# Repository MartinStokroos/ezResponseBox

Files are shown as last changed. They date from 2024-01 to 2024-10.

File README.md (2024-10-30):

# The ezResponseBox
*An open source Button Response Box for 1-8 buttons based on the Raspberry Pi Pico*

Button response boxes are widely utilized in psychological experiments, typically interfaced as serial devices or as Human Interface Devices (HIDs), such as keyboards or joysticks.

The Raspberry Pi Pico serves as a low-cost microcontroller platform. By incorporating an appropriate number of input buttons (1-8) and a plastic enclosure, a response box can be constructed for under $50, offering specifications comparable to many commercial alternatives. The *ezResponseBox* is compatible with software such as [OpenSesame](https://osdoc.cogsci.nl/), PsychoPy, and E-Prime.

The *ezResponseBox* operates as either a keyboard or joystick-type response box, achieving a typical latency of 1 ms (equivalent to a 1000 Hz update rate). This latency is 10 to 20 times lower than that of standard PC keyboards.

In Keyboard Mode I, the *ezResponseBox* transmits keystrokes corresponding to key numbers 1 to 8 based on the pressed button(s). Simultaneous key presses are communicated within the same USB packet, although this occurrence is rare due to the high input scan rate.

In Keyboard Mode II, the *ezResponseBox* transmits two hexadecimal digits ranging from `00` to `FF`. Applications are responsible for decoding simultaneous key presses.

The advantage of using a joystick HID device lies in its ability to send every state change of the inputs to the host as an eight-bit joystick button state. Decoding of the buttons must be performed within the application program.

The *ezResponseBox* scans eight digital inputs to read the current status of the button knobs. Both Normally Open (NO) and Normally Closed (NC) contacts can be utilized. The type of connected button contacts is determined at power-up. NC contacts facilitate faster detection of response onset. The eight input channels are scanned at a rate of 10 kHz, with readings subjected to debouncing via a FIR digital filter algorithm, incorporating a minimum delay of 200µs which lies within the USB package interval. The debounced information is transmitted in the next available USB packet, with only input state changes sent to the computer.

## Specifications
- USB 2.0 compatible
- works under Windows and Linux
- no drivers needed 
- works as a keyboard or as joystick HID-composite device
- 1ms latency (minimum for HID)
- 10kHz input port scan rate
- integrated switch debouncing filter

GP pin vs. keyboard/joystick button number:

pin: | GP0 | GP1 | GP2 | GP3 | GP4 | GP5 | GP6 | GP7
-------- | --- | --- | --- | --- | --- | --- | --- | ---
keypress | '1' | '2' | '3' | '4' | '5' | '6' | '7' | '8'
hex code | 0x01 | 0x02 | 0x04 | 0x08 | 0x10 | 0x20 | 0x40 | 0x80
joystick button | 0 | 1 | 2 | 3 | 4 | 5 | 6 | 7 

## The Input GPIOs
The input pins are: GP0-GP7. The pull-up function is active on all the inputs to allow direct interfacing to pushbutton switches.

## Using NO/NC Button Contacts
By default, the *ezResponseBox* operates with Normally Open (NO) contacts. If at least one connected switch is of the Normally Closed (NC) type, the *ezResponseBox* will detect this upon startup (immediately after connecting to the USB port), resulting in the inversion of all logic input readings. To maintain simplicity, avoid mixing NO and NC contacts. When using NC-type contacts, ensure that unused input pins are tied to the ground (GND pin).

## The Output GPIOs
The eight debounced inputs are mapped to eight digital outputs, specifically GP8 to GP15. The logic state of these outputs can be inverted (refer to *Configuration Settings* below). The logic level is 3.3V; therefore, level converters and/or line drivers are required to interface with external 5V TTL logic or LED indicators.

## Configuration Settings
Upon connecting the *ezResponseBox* to a computer’s USB port, multiple devices may register with the operating system. The only active device is the one selected via jumper wires or DIP switches. Configuration is established at power-up. Refer to the function table below for detailed configuration settings.

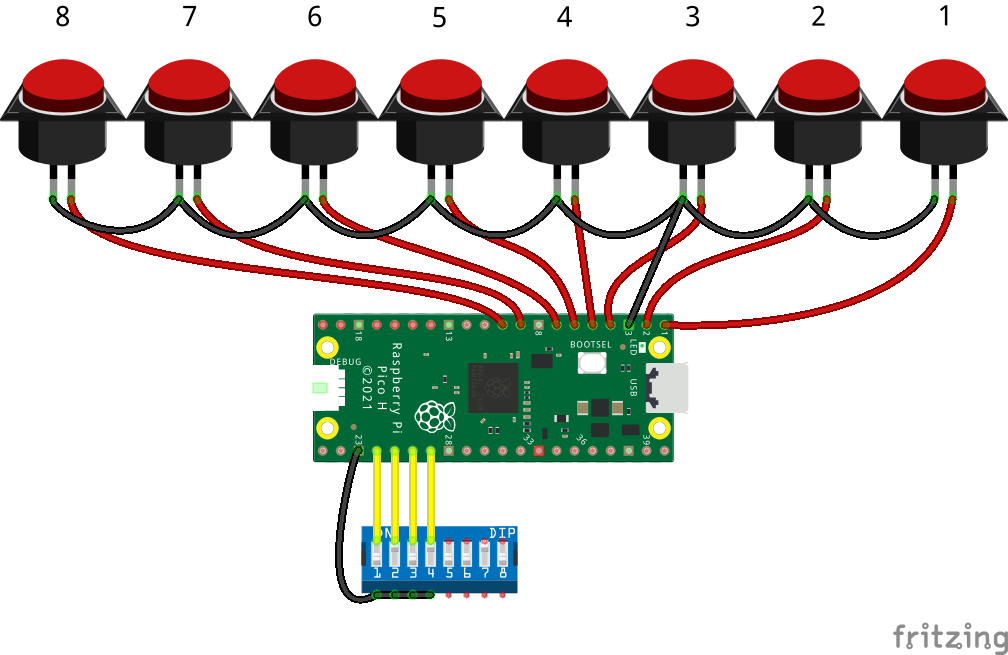
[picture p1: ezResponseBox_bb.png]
wiring diagram


GPIO-pin  | open input | input tied to GND with jumper wire or DIP-switch
--------- | ---------- | ------------------------------------------------
GPIO18 | select keyboard device | select joystick device
GPIO19 | select numerical keys (mode-I) | select hexadecimal digits (mode-II)
GPIO20 | debouncing=ON | debouncing=OFF
GPIO21 | positive logic outputs | negative logic outputs

## Preparing your Raspberry Pico
Hookup one or more buttons to your Pico. Connect the Pico to the PC while pressing and holding the BOOTSEL button. A mass storage device will pop up. Drag the uf2 firmware file into the drive and ready you are! The uf2 firmware file can be found under the release download on this Github page.
This firmware was tested with the Raspberry Pi Pico (without W).

## A 10$ Button Box
A two button response box | bottom side
------------------------- | -----------
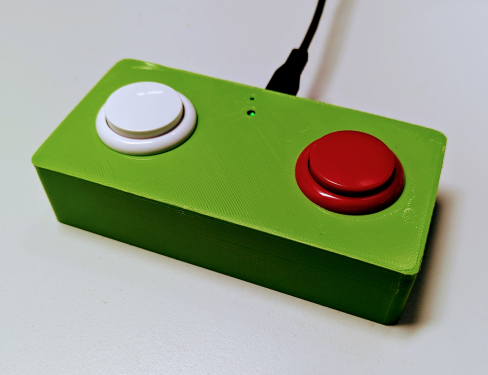
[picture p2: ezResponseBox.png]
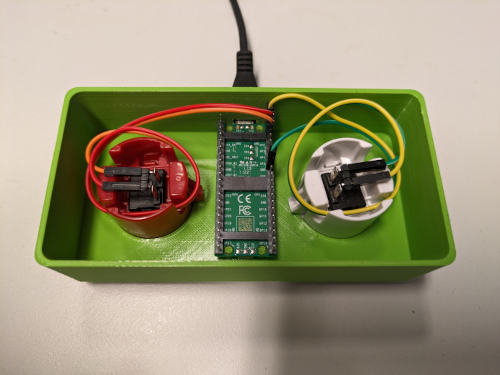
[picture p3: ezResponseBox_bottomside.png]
 | 

## Known bugs
- Displays only one "0"-character in keyboard mode-II for the 0-state code in some text editors or terminal programs. In real, double zeros are sent.
- The color of the prototype:)

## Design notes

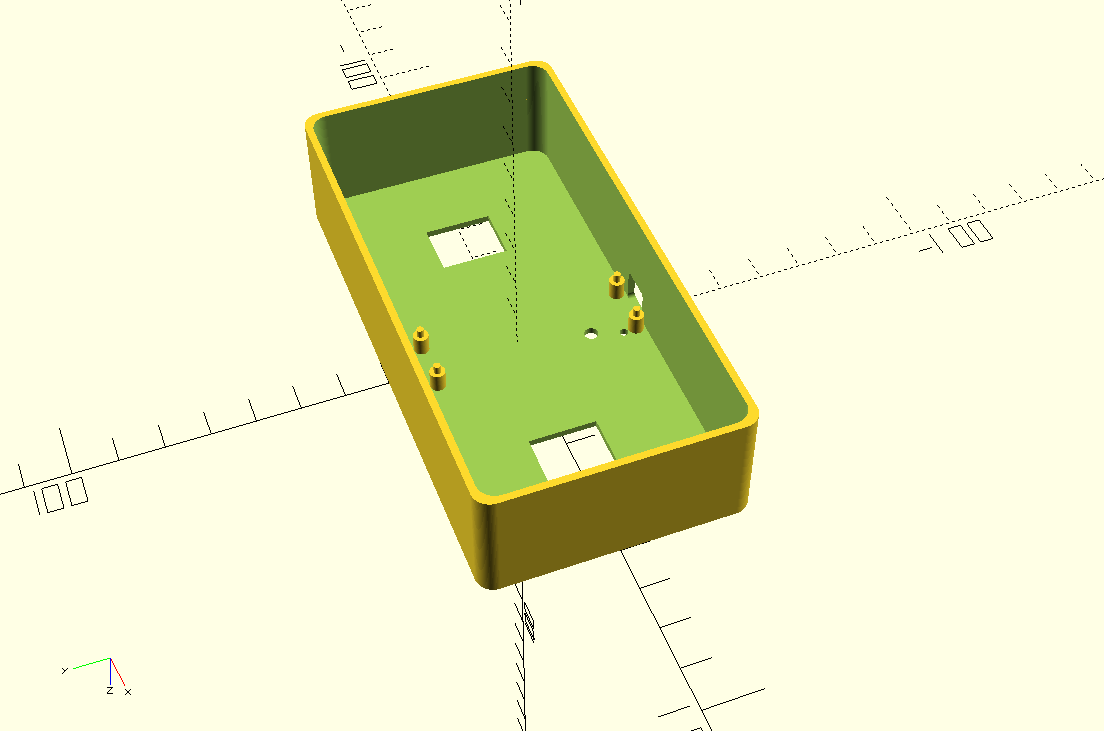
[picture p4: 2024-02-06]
enclosure/ezResponseBox.png

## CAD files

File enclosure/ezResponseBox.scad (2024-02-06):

/*
 * MIT License
 *
 * Copyright (c) 2023 Martin Stokroos
 *
 * Permission is hereby granted, free of charge, to any person obtaining a copy 
 * of this software and associated documentation files (the "Software"), to deal
 * in the Software without restriction, including without limitation the rights 
 * to use, copy, modify, merge, publish, distribute, sublicense, and/or sell 
 * copies of the Software, and to permit persons to whom the Software is 
 * furnished to do so, subject to the following conditions:
 *
 * The above copyright notice and this permission notice shall be included in 
 * all copies or substantial portions of the Software.
 *
 * THE SOFTWARE IS PROVIDED "AS IS", WITHOUT WARRANTY OF ANY KIND, EXPRESS OR 
 * IMPLIED, INCLUDING BUT NOT LIMITED TO THE WARRANTIES OF MERCHANTABILITY, 
 * FITNESS FOR A PARTICULAR PURPOSE AND NONINFRINGEMENT. IN NO EVENT SHALL THE
 * AUTHORS OR COPYRIGHT HOLDERS BE LIABLE FOR ANY CLAIM, DAMAGES OR OTHER
 * LIABILITY, WHETHER IN AN ACTION OF CONTRACT, TORT OR OTHERWISE, ARISING FROM,
 * OUT OF OR IN CONNECTION WITH THE SOFTWARE OR THE USE OR OTHER DEALINGS IN
 * THE SOFTWARE.
 *
 */

// ezResponseBox enclosure for two buttons.
//
// This is a simple OpenSCAD design sketch for a 3D printable response box enclosure.
// This design is screwless. To fixate the pico, melt the (PLA)plastic pins downwards 
// with a (not too) hot iron nail.

length = 120; //dimensions in mm.
width = 60;
height = 28;
wt = 1.6; // wall thickness
poffs = 2.1; // pico spacers, offset from the inner edge (USB-side)
pindia = 1.6; // pico fixation pin diameter
knob_spacing = 34;

difference(){
    union(){
        difference(){
            translate([0,0,-height/2]) roundCornersCube(length, width, height, 4.0); //outline
            translate([0,0,-height/2-wt]) roundCornersCube(length-2*wt, width-2*wt, height, 4.0); //cutout
        }
        // spacers for the PICO
        translate([5.7, -width/2+wt+poffs, -6.0]) cylinder(d=3.5, h=5, center=false, $fn=150); //USB side
        translate([-5.7, -width/2+wt+poffs, -6.0]) cylinder(d=3.5, h=5, center=false, $fn=150); //USB side
        translate([5.7, -width/2+wt+51-poffs, -6.0]) cylinder(d=3.5, h=5, center=false, $fn=150);
        translate([-5.7, -width/2+wt+51-poffs, -6.0]) cylinder(d=3.5, h=5, center=false, $fn=150);
        
        translate([5.7, -width/2+wt+poffs, -8.0]) cylinder(d=pindia, h=6, center=false, $fn=150); //USB side
        translate([-5.7, -width/2+wt+poffs, -8.0]) cylinder(d=pindia, h=6, center=false, $fn=150); //USB side
        translate([5.7, -width/2+wt+51-poffs, -8.0]) cylinder(d=pindia, h=6, center=false, $fn=150);
        translate([-5.7, -width/2+wt+51-poffs, -8.0]) cylinder(d=pindia, h=6, center=false, $fn=150);
    }
      
    // Mark's knob
    //translate([-knob_spacing, 0, 0]) cylinder(d=30.4, h=20, center=true, $fn=150);
    //translate([knob_spacing, 0, 0]) cylinder(d=30.4, h=20, center=true, $fn=150);
    
    // Standard knobs, use your own knob cut out pattern.
    translate([34, 0, 0])cube([12.5, 15.5, 10], center=true);
    translate([-34, 0, 0])cube([12.5, 15.5, 10], center=true);
    
    // Opening for the USB connector.
    translate([0, -width/2+0.2, -8.0/2-wt]) rotate([90,0,0]) roundCornersCube(8.0, 8, 3.0, 1);
    // Hole for pico bootsel button.
    translate([3.7, -width/2+wt+poffs+10, -3]) cylinder(d=3.2, h=6, center=false, $fn=150);
    // Hole for pico LED.
    translate([6, -width/2+wt+poffs+3, -3]) cylinder(d=2, h=6, center=false, $fn=150);
}



/*
roundCornersCube is licensed under the GNU license.

Copyright (C) 2011 Sergio Vilches

This program is free software: you can redistribute it and/or modify it under the terms of the GNU General Public License as published by the Free Software Foundation, either version 3 of the License, or (at your option) any later version.
This program is distributed in the hope that it will be useful, but WITHOUT ANY WARRANTY; without even the implied warranty of MERCHANTABILITY or FITNESS FOR A PARTICULAR PURPOSE. See the GNU General Public License for more details. You should have received a copy of the GNU General Public License along with this program. If not, see <http://www.gnu.org/licenses/>.
Contact: s.vilches.e@gmail.com


    ----------------------------------------------------------- 
                 Round Corners Cube (Extruded)            
      roundCornersCube(x,y,z,r) Where:                        
         - x = Xdir width                                     
         - y = Ydir width                                     
         - z = Height of the cube                             
         - r = Rounding radious                               
                                                              
      Example: roundCornerCube(10,10,2,1);                    
     *Some times it's needed to use F6 to see good results!   
 	 ---------------------------------------------------------- 
*/

module createMeniscus(h,radius) // This module creates the shape that needs to be substracted from a cube to make its corners rounded.
difference(){        //This shape is basicly the difference between a quarter of cylinder and a cube
   translate([radius/2+0.1,radius/2+0.1,0]){
      cube([radius+0.2,radius+0.1,h+0.2],center=true);         // All that 0.x numbers are to avoid "ghost boundaries" when substracting
   }

   cylinder(h=h+0.2,r=radius,$fn = 100,center=true);
}


module roundCornersCube(x,y,z,r)  // Now we just substract the shape we have created in the four corners
difference(){
   cube([x,y,z], center=true);

translate([x/2-r,y/2-r]){  // We move to the first corner (x,y)
      rotate(0){  
         createMeniscus(z,r); // And substract the meniscus
      }
   }
   translate([-x/2+r,y/2-r]){ // To the second corner (-x,y)
      rotate(90){
         createMeniscus(z,r); // But this time we have to rotate the meniscus 90 deg
      }
   }
      translate([-x/2+r,-y/2+r]){ // ... 
      rotate(180){
         createMeniscus(z,r);
      }
   }
      translate([x/2-r,-y/2+r]){
      rotate(270){
         createMeniscus(z,r);
      }
   }
}

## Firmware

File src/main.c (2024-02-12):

/* 
 * The MIT License (MIT)
 *
 * Copyright (c) 2019 Ha Thach (tinyusb.org)
 *
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
 */
 
/*
 * MIT License
 *
 * Copyright (c) 2023 Martin Stokroos (ezResponseBox)
 *
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
 */

#include <stdlib.h>
#include <stdio.h>
#include <string.h>
#include "hardware/gpio.h"
#include "pico/util/queue.h"

#include "bsp/board.h"
#include "tusb.h"
#include "usb_descriptors.h"

#define HZ 100  //digital input sampling delay in us.
#define NCHAN 8 //max number of input/output channels = 8
#define FIRST_GPIO_IN 0
#define FIRST_GPIO_OUT (FIRST_GPIO_IN + 8)
#define RANGE_GPIO 0xFFFF
#define KEY_JOY_SEL_PIN 18
#define KEY_MODE_SEL_PIN 19
#define DEBOUNCE_SEL_PIN 20
#define INVERT_OUTPUTS_SEL_PIN 21

//--------------------------------------------------------------------+
// MACRO CONSTANT TYPEDEF PROTYPES
//--------------------------------------------------------------------+

/* Blink pattern
 * - 250 ms  : device not mounted
 * - 1000 ms : device mounted
 * - 2500 ms : device is suspended
 */
enum {
  BLINK_NOT_MOUNTED = 250,
  BLINK_MOUNTED = 1000,
  BLINK_SUSPENDED = 2500,
};

// prototypes
void led_blinking_task(void);
void hid_task(void);
static void send_hid_report(uint8_t report_id);
bool timer_callback(repeating_timer_t *rt);
void to_hex(uint8_t* in, uint8_t* out);
void to_keycode(uint8_t* in, size_t insz, uint8_t* out);

// globals
static uint32_t blink_interval_ms = BLINK_NOT_MOUNTED;
static uint32_t portsAll;
static uint8_t newEvent, lastEvent, xMask;
static bool eventUpdate;
typedef struct {
  bool ncContacts;
  bool deviceMode;
  bool keyMode;
  bool debounceOn;
  bool invertOp;
} ezConfig;
ezConfig config;

static uint8_t window[8] = {0, 0, 0, 0, 0, 0, 0, 0}; // store 8-ch parallel window data
static const uint8_t filtered[32] =
{
  0,  //00000
  0,  //00001
  0,  //00010
  1,  //00011
  0,  //00100
  1,  //00101
  1,  //00110
  1,  //00111
  0,  //01000
  1,  //01001
  1,  //01010
  1,  //01011
  1,  //01100
  1,  //01101
  1,  //01110
  1,  //01111
  0,  //10000
  0,  //10001
  0,  //10010
  1,  //10011
  0,  //10100
  1,  //10101
  1,  //10110
  1,  //10111
  0,  //11000
  1,  //11001
  1,  //11010
  1,  //11011
  1,  //11100
  1,  //11101
  1,  //11110
  1   //11111
};


/*------------- MAIN -------------*/
int main(void)
{
  gpio_init(KEY_JOY_SEL_PIN);
  gpio_init(KEY_MODE_SEL_PIN);
  gpio_init(DEBOUNCE_SEL_PIN);
  gpio_init(INVERT_OUTPUTS_SEL_PIN);
  gpio_set_dir(KEY_JOY_SEL_PIN, GPIO_IN);
  gpio_set_dir(KEY_MODE_SEL_PIN, GPIO_IN);
  gpio_set_dir(DEBOUNCE_SEL_PIN, GPIO_IN);
  gpio_set_dir(INVERT_OUTPUTS_SEL_PIN, GPIO_IN);
  gpio_pull_up(KEY_JOY_SEL_PIN);
  gpio_pull_up(KEY_MODE_SEL_PIN);
  gpio_pull_up(DEBOUNCE_SEL_PIN);
  gpio_pull_up(INVERT_OUTPUTS_SEL_PIN);

  // Read the hardware configuration status
  config.deviceMode = gpio_get(KEY_JOY_SEL_PIN);
  config.keyMode = gpio_get(KEY_MODE_SEL_PIN);
  config.debounceOn = gpio_get(DEBOUNCE_SEL_PIN);
  config.invertOp = gpio_get(INVERT_OUTPUTS_SEL_PIN);

  for (int gpio = FIRST_GPIO_IN; gpio < FIRST_GPIO_IN + NCHAN; gpio++)
  {
    gpio_init(gpio);
    gpio_set_dir(gpio, GPIO_IN);
    gpio_pull_up(gpio);
  }

  for (int gpio = FIRST_GPIO_OUT; gpio < FIRST_GPIO_OUT + NCHAN; gpio++)
  {
    gpio_init(gpio);
    gpio_set_dir(gpio, GPIO_OUT);
    if(!config.invertOp) {
      gpio_set_outover(gpio, GPIO_OVERRIDE_INVERT); //invert output channels
    }
  }  

  // Detect if one or more switches are NC and pulling down the input.
  portsAll = ~gpio_get_all(); // Read all gpio's (29-0) at once and bitwise invert.
  portsAll = portsAll >> FIRST_GPIO_IN;
  if ((portsAll & 0xFF) > 0) // Use bitmask for 8 bits. (Size of NCHAN could be different!)
  {
    config.ncContacts = true;
  }

  board_init();
  tusb_init();

  repeating_timer_t timer;
  // negative timeout means exact delay in us (rather than delay between callbacks)
  if (!add_repeating_timer_us(-HZ, timer_callback, NULL, &timer)) {
    //printf("Failed to add timer\n");
    return 1;
  }

  while (1)
  {
    tud_task(); // tinyusb device task
    led_blinking_task();

    hid_task();
    //cancel_repeating_timer(&timer);
  }
}



//--------------------------------------------------------------------+
// Device callbacks
//--------------------------------------------------------------------+

// Invoked when device is mounted
void tud_mount_cb(void)
{
  blink_interval_ms = BLINK_MOUNTED;
}

// Invoked when device is unmounted
void tud_umount_cb(void)
{
  blink_interval_ms = BLINK_NOT_MOUNTED;
}

// Invoked when usb bus is suspended
// remote_wakeup_en : if host allow us  to perform remote wakeup
// Within 7ms, device must draw an average of current less than 2.5 mA from bus
void tud_suspend_cb(bool remote_wakeup_en)
{
  (void) remote_wakeup_en;
  blink_interval_ms = BLINK_SUSPENDED;
}

// Invoked when usb bus is resumed
void tud_resume_cb(void)
{
  blink_interval_ms = BLINK_MOUNTED;
}


//--------------------------------------------------------------------+
// USB HID
//--------------------------------------------------------------------+

// Invoked when sent REPORT successfully to host
// Application can use this to send the next report
// Note: For composite reports, report[0] is report ID
void tud_hid_report_complete_cb(uint8_t instance, uint8_t const* report, uint16_t len)
{
  (void) instance;
  (void) len;
}


// Invoked when received GET_REPORT control request
// Application must fill buffer report's content and return its length.
// Return zero will cause the stack to STALL request
uint16_t tud_hid_get_report_cb(uint8_t instance, uint8_t report_id, hid_report_type_t report_type, uint8_t* buffer, uint16_t reqlen)
{
  // TODO not Implemented
  (void) instance;
  (void) report_id;
  (void) report_type;
  (void) buffer;
  (void) reqlen;

  return 0;
}


// Invoked when received SET_REPORT control request or
// received data on OUT endpoint ( Report ID = 0, Type = 0 )
void tud_hid_set_report_cb(uint8_t instance, uint8_t report_id, hid_report_type_t report_type, uint8_t const* buffer, uint16_t bufsize)
{
  (void) instance;

  if (report_type == HID_REPORT_TYPE_OUTPUT)
  {
    // Set keyboard LED e.g Capslock, Numlock etc...
    if (report_id == REPORT_ID_KEYBOARD)
    {
      // bufsize should be (at least) 1
      if ( bufsize < 1 ) return;

      uint8_t const kbd_leds = buffer[0];

      if (kbd_leds & KEYBOARD_LED_CAPSLOCK)
      {
        // Capslock On: disable blink, turn led on
        blink_interval_ms = 0;
        board_led_write(true);
      } else
      {
        // Caplocks Off: back to normal blink
        board_led_write(false);
        blink_interval_ms = BLINK_MOUNTED;
      }
    }
  }
}



//--------------------------------------------------------------------+
// BLINKING TASK
//--------------------------------------------------------------------+
void led_blinking_task(void)
{
  static uint32_t start_ms = 0;
  static bool led_state = false;

  // blink is disabled
  if (!blink_interval_ms) return;

  // Blink every interval ms
  if ( board_millis() - start_ms < blink_interval_ms) return; // not enough time
  start_ms += blink_interval_ms;

  board_led_write(led_state);
  led_state = 1 - led_state; // toggle
}



//--------------------------------------------------------------------+
// HID TASK
//--------------------------------------------------------------------+
void hid_task(void)
{
  // Remote wakeup
  if ( tud_suspended() && eventUpdate) {
    // Wake up host if we are in suspend mode
    // and REMOTE_WAKEUP feature is enabled by host
    tud_remote_wakeup();
  } else
  {
    if(config.deviceMode == true) {
      send_hid_report(REPORT_ID_KEYBOARD);
    } else {
      send_hid_report(REPORT_ID_GAMEPAD);
    }
  }
}



//--------------------------------------------------------------------+
// SEND HID REPORT
//--------------------------------------------------------------------+
static void send_hid_report(uint8_t report_id)
{
  // skip if hid is not ready yet
  if ( !tud_hid_ready() ) return;


  switch(report_id)
  {
    case REPORT_ID_KEYBOARD:
    {
      // use to avoid send multiple consecutive zero report for keyboard
      static bool has_keyboard_key = false;
      uint8_t keycode[6] = { 0 };

      if ( eventUpdate )
      {
        if(config.keyMode == true) {
          if(lastEvent == 0) { // input changed to zero
            tud_hid_keyboard_report(REPORT_ID_KEYBOARD, 0, NULL);
          }
          else
          {
            // Handling multiple (n=6 max) changes at once.
            // In practice, detecting a double key hit will be seldom,
            // because of the high sampling rate. n set to 3.
            uint8_t k, n=0;
            for(k = 0; k < NCHAN; k++) {
              if((lastEvent >> k) & (xMask >> k) & 1) {
                keycode[n] = HID_KEY_1 + k;
                n++;
              }
              if(n > 2) break;
              //keycode[0] = n + 0x1D; // for double hit debugging purpose
            }
          }
          tud_hid_keyboard_report(REPORT_ID_KEYBOARD, 0, keycode);
        } else { // output hex
          enum { hexsz = 2 };
          uint8_t hexcode[hexsz]; // create target array
          to_hex(&lastEvent, hexcode);
          to_keycode(hexcode, hexsz, keycode);
          tud_hid_keyboard_report(REPORT_ID_KEYBOARD, 0, keycode);
          has_keyboard_key = true;
        }
      eventUpdate = false;
      }
      else {
        // send empty key report if previously has key pressed
        if (has_keyboard_key) tud_hid_keyboard_report(REPORT_ID_KEYBOARD, 0, NULL);
        has_keyboard_key = false;
      }
    }
    break;

    case REPORT_ID_GAMEPAD:
    {
      hid_gamepad_report_t report = {
        .x   = 0, .y = 0, .z = 0,
        .rz = 0, .rx = 0, .ry = 0,
        .hat = 0, 
        .buttons = 0
      };

      if ( eventUpdate ) {
        report.buttons = lastEvent;
        // report.hat = 0 // completing axis data, etc.
        tud_hid_report(REPORT_ID_GAMEPAD, &report, sizeof(report));
        eventUpdate = false;
      }
    }
    break;

    default: break;
  }
}



//--------------------------------------------------------------------+
// Converts a byte to a hexadecimal character string
//
//--------------------------------------------------------------------+
void to_hex(uint8_t* in, uint8_t* out) {
  uint8_t *pin = in;
  const char *hex = "0123456789ABCDEF";
  uint8_t *pout = out;

  *pout++ = hex[(*pin >> 4) & 0xF];
  *pout++ = hex[(*pin++) & 0xF];
  //*pout = 0;
}



//--------------------------------------------------------------------+
// Converts hexadecimal character string to keyboard scan codes
//
//--------------------------------------------------------------------+
void to_keycode(uint8_t* in, size_t insz, uint8_t* out) {
  uint8_t *pin = in;
  uint8_t *pout = out;
  int i = 0;

  for(; i < insz; ++i) {
    if(*pin > 0x40) {  // if ascii letter...
      *pout++ = *pin++ - 0x3D;
    }
    else if(*pin == 0x30) {  // if ascii zero...
      *pout++ = *pin++ - 0x09;
    }
    else {
      *pout++ = *pin++ - 0x13;  // else ascii number...
    }
  }
  *pout = 0;
}
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

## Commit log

2023-10-10 sample rate to 5k
2024-02-06 add enclosure + lic
    [ezResponseBox.scad]
